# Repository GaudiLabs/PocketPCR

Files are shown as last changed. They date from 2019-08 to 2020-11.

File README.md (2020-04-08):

# PocketPCR
Pocket size USB powered PCR Thermo Cycler.

For more information see project website:
http://gaudi.ch/PocketPCR/

Designed by GaudiLabs:
http://www.gaudi.ch/GaudiLabs/

Support the development of Open Science Hardware:
https://gaudishop.ch/

### License

PocketPCR, all design files and software are licensed under a GNU GENERAL PUBLIC LICENSE
See license file in the repository.

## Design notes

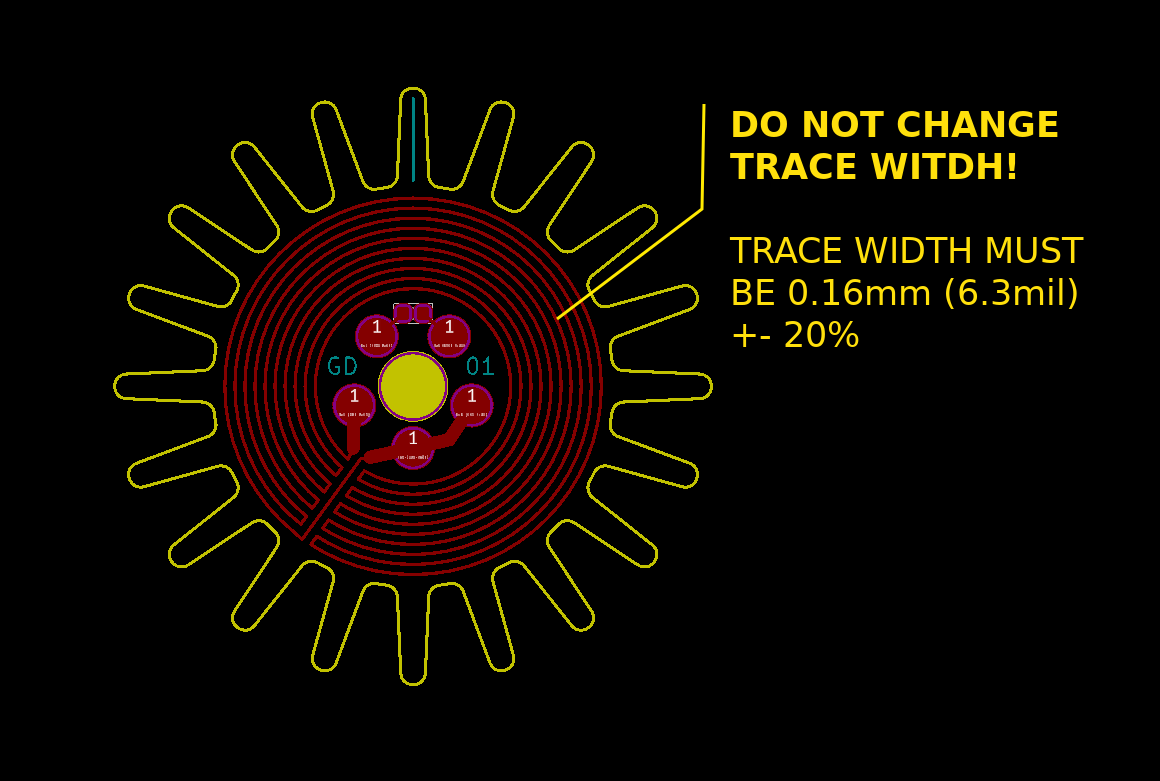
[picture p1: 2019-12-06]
PCB_Layouts/PocketPCR_BottomHeater/Gerber/ProductionFiles/w16496axn77/yg/W16496AXN77_PCR_BottomHeater/W16496AXN77_PCR_BottomHeater/Production_Note.png

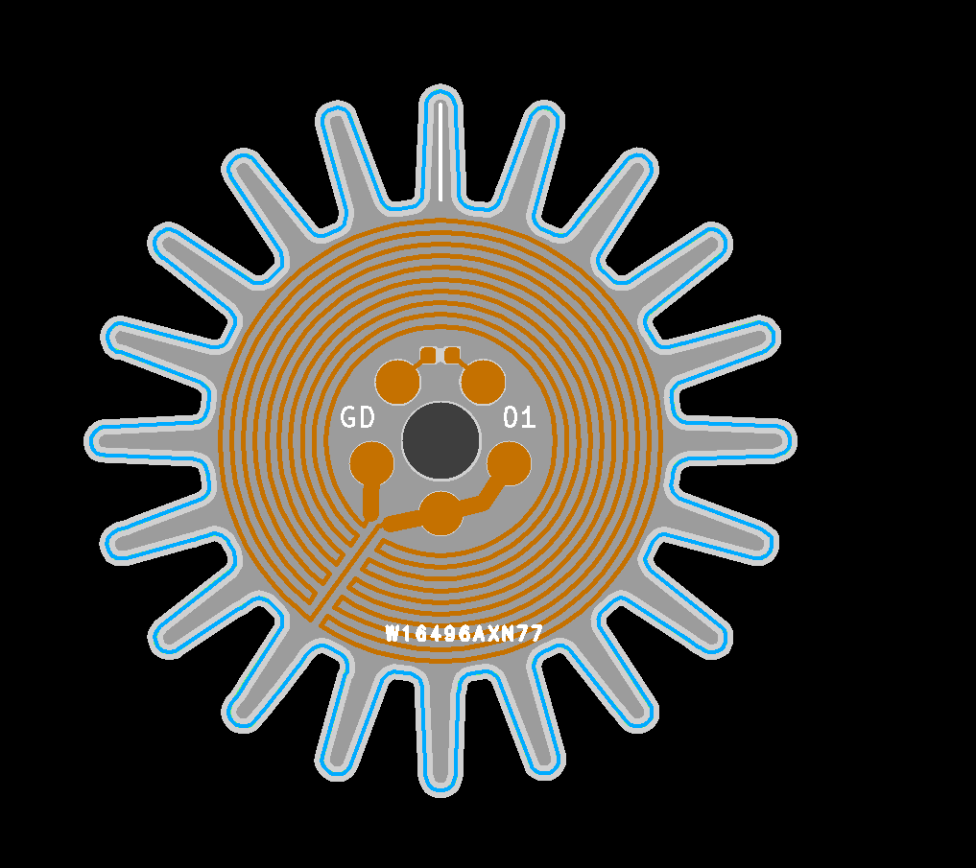
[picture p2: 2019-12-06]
PCB_Layouts/PocketPCR_BottomHeater/BottomHeaterProductionFiles.png

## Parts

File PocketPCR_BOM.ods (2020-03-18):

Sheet: RocketPCR
BOM PocketPCR |  | 19. February 2020
Designator | Quantity | Designation | Package | Order No
U2 | 1 | SAMD21G18B-A changed from SAML21 | TQFP-48_7x7mm_Pitch0.5mm | 556-ATSAMD21G18A-AUT
S1 | 1 | OLED Connector |  | 649-SFV30R-1STE1HLF
Y1 | 1 | Crystal 32.765 | Crystal_SMD_3215-2pin_3.2x1.5mm | 520-ECS-327-12.5-34B 449-LFXTAL009678REEL
LED2,LED1 | 2 | LED | LED-0805
U1 | 1 | TLV1117-33 | SOT-223 | 595-TLV1117LV33DCYR
Q2,Q1,Q3 | 3 | Q_NMOS_GSD | SOT-23 | 863-NTR3C21NZT1G
C3 | 1 | 100uF,6.3V | C_1206_3216Metric | JMK316ABJ107ML-T
C2,C5 | 2 | 10uF, 6.3V | C_1206_3216Metric | JMK107ABJ106MA-T
C1,C4,C12,C14,C16 | 5 | 1uF | C_0805_2012Metric | 810-C2012X7R1C105M-3 603-CC805KKX7R7BB105
C6,C7,C8,C9 | 4 | 100nF | C_0805_2012Metric
C10,C11 | 2 | 22pF | C_0805_2012Metric
C15,C17 | 2 | 2.2uF | C_0805_2012Metric | 603-CC805KKX7R7BB225
R1,R9,R10 | 1 | 4.7k | R_0805_2012Metric
R2,R3 | 2 | 390Ohm | R_0805_2012Metric
R5, R7 | 2 | 390k | R_0805_2012Metric
R4, R6 | 1 | 4.7k 0.1% |  | 279-CPF0805B4K7E1
J3 | 1 | USB_C_Receptacle | USB_C_Receptacle_Amphenol_12401610E4-2A | 523-12401610E4#2A
NTC | 1 | NTC-Thermistoren 0402 10K OHM 0.5% |  | 810-NTCG103JX103DTDS
S1 | 1 | OLED_DISPLAY | OLED_096_1_Flip
J2 | 0 | Conn_02x05_Odd_Even | Pin_Header_Straight_2x05_Pitch1.27mm_SMD
PCB1 | 1 | TopHeater PCB | Alluminium Board, Conductivity 2W, 1.6mm, Black
PCB2 | 1 | PocketPCR PCB | FR4, Black, Thickness 1.6mm
PCB3 | 1 | Lid PCB | FR4, White,Thickness 1.2mm
X1 | 2 | Distanzhülsen, Metall, 6-Kant, M3, 10mm |  | VT DI 10MM
X2 | 2 | Distanzhülsen, Metall, 6-Kant, M3, 20mm |  | VT DI 20MM
SW1 | 1 | Rotary_Encoder_Switch | RotaryEncoder_Alps_EC11E-Switch_Vertical_H20mm | 858-EN11-HSB1AQ15
 | 1 | Encoder Cap | 100Pcs Potentiometer Volume Control/ Switch Knobs Kits 6mm (1/4inch) Shaft
 | 1 | Spring |  | Wire Dia: 0.4mm / Length: 5 mm Or Wire Dia: 0.3mm / Length: 10 mm
 | 1 | Plastic Screw | White Nylon Insulating Countersunk Flat Phillips head Screw M2.5 M3 M4 | M3*6mm
 | 1 | Plastic Screw | 25 BLACK Nylon Plastic M3 M4 M5 and M6 Thumbscrews Knurled + Slotted Thumb Screw | Screw Length: 25mm / M3
 | 2 | Screw | Linsenkopfschraube mit Kreuzschlitz M 3 x 6 DIN 7985 Edelstahl Schwarz 100 Stk.
 | 4 | Screw | Linsenkopfschraube mit Kreuzschlitz M 3 x 16 DIN 7985 Edelstahl Schwarz 100 Stk.
 | 4 | Feets | MAKSEY Rubber Male Hole caps Silicone T type Plug Stopper 6.5mm 7mm 7.5mm 8mm 8.5m Plastic Round Test Tube end caps Gap Masking | Black + 2.7mm
 | 1 | Blower | DIY Reprap 3010 fan 30MM 30x30x10MM 12V 5V 2Pin DC Cooler Small Cooling Fan For 3D Pinter | 5V
J1 | 1 | Conn_01x02_Male | PinHeader_1x02_P2.54mm_Vertical
 | 1 | Beutel ESD | ESD PE-Abschirmbeutel, wiederverschließbar, 76 x 127 mm | ESD BEUTEL-S 127
 | 1 | Heat Block | Aluminium Rund EN AW-6082, gezogen 20 mm | 19.5mm

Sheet: RocketPCR_2
BOM PocketPCR
Designator | Quantity | Designation | Package | Order No | Unit Price | Price
U2 | 1 | SAMD21G18B-A changed from SAML21 | TQFP-48_7x7mm_Pitch0.5mm | 556-ATSAMD21G18A-AUT | 3.16 | 3.16
S1 | 1 | OLED_DISPLAY | OLED_096_1_Flip |  | 3 | 3
 | 1 | TopHeater |  | 19.5mm | 2.5 | 2.5
J3 | 1 | USB_C_Receptacle | USB_C_Receptacle_Amphenol_12401610E4-2A | 523-12401610E4#2A | 1.94 | 1.94
SW1 | 1 | Rotary_Encoder_Switch | RotaryEncoder_Alps_EC11E-Switch_Vertical_H20mm | 858-EN11-HSB1AQ15 | 1.71 | 1.71
S1 | 1 | OLED Connector |  | 649-SFV30R-1STE1HLF | 0.85 | 0.85
PCB2 | 1 | PocketPCR PCB |  |  | 0.825 | 0.825
Q2,Q1,Q3 | 3 | Q_NMOS_GSD | SOT-23 | 863-NTR3C21NZT1G | 0.264 | 0.792
 | 1 | Blower | DIY Reprap 3010 fan 30MM 30x30x10MM 12V 5V 2Pin DC Cooler Small Cooling Fan For 3D Pinter | 5V | 0.65 | 0.65
X2 | 2 | Distanzhülsen, Metall, 6-Kant, M3, 20mm |  | VT DI 20MM | 0.297 | 0.594
U1 | 1 | TLV1117-33 | SOT-223 | 595-TLV1117LV33DCYR | 0.547 | 0.547
PCB1 | 1 | TopHeater PCB |  |  | 0.5 | 0.5
C15,C17 | 2 | 2.2uF | C_0805_2012Metric | 603-CC805KKX7R7BB225 | 0.233 | 0.466
 | 4 | Feets | MAKSEY Rubber Male Hole caps Silicone T type Plug Stopper 6.5mm 7mm 7.5mm 8mm 8.5m Plastic Round Test Tube end caps Gap Masking | Black + 2.7mm | 0.1 | 0.4
Y1 | 1 | Crystal 32.765 | Crystal_SMD_3215-2pin_3.2x1.5mm | 449-LFXTAL009678REEL | 0.398 | 0.398
 | 4 | Screw | Linsenkopfschraube mit Kreuzschlitz M 3 x 16 DIN 7985 Edelstahl Schwarz 100 Stk. |  | 0.09845 | 0.3938
X1 | 2 | Distanzhülsen, Metall, 6-Kant, M3, 10mm |  | VT DI 10MM | 0.143 | 0.286
 | 1 | Spring |  |  | 0.279 | 0.279
C4,C1,C12,C14,C16 | 5 | 1uF | C_0805_2012Metric |  | 0.05 | 0.25
PCB3 | 1 | Lid PCB |  |  | 0.25 | 0.25
 | 1 | Plastic Screw | 25 BLACK Nylon Plastic M3 M4 M5 and M6 Thumbscrews Knurled + Slotted Thumb Screw | Screw Length: 25mm / M3 | 0.2268 | 0.2268
C6,C7,C8,C9 | 4 | 100nF | C_0805_2012Metric |  | 0.05 | 0.2
 | 2 | Screw | Linsenkopfschraube mit Kreuzschlitz M 3 x 6 DIN 7985 Edelstahl Schwarz 100 Stk. |  | 0.09845 | 0.1969
 | 1 | NTC-Thermistoren 0402 10K OHM 0.5% |  | 810-NTCG103JX103DTDS | 0.18 | 0.18
 | 1 | Encoder Cap | 100Pcs Potentiometer Volume Control/ Switch Knobs Kits 6mm (1/4inch) Shaft |  | 0.1654 | 0.1654
R4 | 1 | 4.7k 0.1% |  | 279-CPF0805B4K7E1 | 0.149 | 0.149
C10,C11 | 2 | 22pF | C_0805_2012Metric |  | 0.05 | 0.1
C2 | 1 | 100uF,35V | C_1206_3216Metric |  | 0.1 | 0.1
C3,C5 | 2 | 22uF | C_1206_3216Metric |  | 0.05 | 0.1
 | 1 | Plastic Screw | White Nylon Insulating Countersunk Flat Phillips head Screw M2.5 M3 M4 | M3*6mm | 0.0598 | 0.0598
R2,R3 | 2 | 390Ohm | R_0805_2012Metric |  | 0.01 | 0.02
R9,R10 | 2 | 5k | R_0805_2012Metric |  | 0.01 | 0.02
R1 | 1 | 10k | R_0805_2012Metric |  | 0.01 | 0.01
R5 | 1 | 100k | R_0805_2012Metric |  | 0.01 | 0.01
R7 | 1 | 390k | R_0805_2012Metric |  | 0.01 | 0.01
J1 | 1 | Conn_01x02_Male | PinHeader_1x02_P2.54mm_Vertical |  |  | 0
J2 | 1 | Conn_02x05_Odd_Even | Pin_Header_Straight_2x05_Pitch1.27mm_SMD |  |  | 0
LED2,LED1 | 2 | LED | LED-0805 |  |  | 0
 |  |  |  |  |  | 0
 |  |  |  |  | 18.9739 | 21.3387
 |  |  |  |  |  | 0.576417494973921

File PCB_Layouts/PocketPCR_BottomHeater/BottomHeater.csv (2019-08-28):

Id | Designator | Package | Quantity | Designation | Supplier and ref
1 | D2 | LCC3_SMD | 1 | APD
2 | C1 | C_0805_HandSoldering | 1 | 1uF
3 | C2 | C_0805_HandSoldering | 1 | 0.047uF/200 V(smaller)
4 | C3 | C_0805_HandSoldering | 1 | 0.1uF / 200V
5 | C4 | C_0805_HandSoldering | 1 | 0.22uF
6 | C5 | C_0805_HandSoldering | 1 | 0.1uF
7 | C6 | C_0805_HandSoldering | 1 | 0.5-1pF
8 | R1 | R_0805_HandSoldering | 1 | 4k
9 | R2,R3 | R_0805_HandSoldering | 2 | 1.2M (0)
10 | R4 | R_0805_HandSoldering | 1 | 3.3k
11 | R5 | R_0805_HandSoldering | 1 | 2.2M (1M)
12 | R6 | R_0805_HandSoldering | 1 | 24.9k
13 | R7 | R_0805_HandSoldering | 1 | 20k (higher?)
14 | R8 | R_0805_HandSoldering | 1 | 32.4k
15 | R9,R10 | R_0805_HandSoldering | 2 | 100k
16 | U1 | QFN-12_4x4 | 1 | MAX1932
17 | VREF | PAD_SMD_3mm | 1 | AREF
18 | JP2,JP1 | GS3 | 2 | Jumper_NC_Dual
19 | D1 | SMB_Handsoldering | 1 | 220V
20 | D3 | TOPLED | 1 | LED
21 | L1 | Choke_SMD_7.3x7.3_H3.5 | 1 | 250uH / 0.1A
22 | R11 | R_0805_HandSoldering | 1 | <1G Ohm
23 | SW1 | PUSH_BUTTON_SMD | 1 | BUT
24 | SW2 | DC_JACK_SMD | 1 | DC_JACK
25 | U2 | ARDUINO_MICRO_SMD | 1 | ARDUINO_MICRO
26 | U3 | SOIC-08_N | 1 | OPA656
27 | VBIAS | PAD_SMD_3mm | 1 | VBiasM
28 | GND | PAD_SMD_3mm | 1 | GND
29 | N1,N2 | SOT-23 | 2 | BSS131
30 | R12 | R_0805_HandSoldering | 1 | 10k
31 | TH1 | R_0805_HandSoldering | 1 | Thermistor_NTC 10k
32 | X2 | PAD_SMD_4x2mm | 1 | P+
33 | X3 | PAD_SMD_4x2mm | 1 | P-
34 | G***,G*** | OpenAPD_Photonpack2 | 2 | LOGO
35 | G*** | OpenHardwareLogo | 1 | LOGO
36 | BLOW- | PAD_SMD_3mm | 1 | BLOWER+
37 | BLOW+ | PAD_SMD_3mm | 1 | BLOWER-

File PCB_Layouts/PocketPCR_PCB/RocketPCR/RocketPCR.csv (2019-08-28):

Id | Designator | Package | Quantity | Designation | Supplier and ref
1 | L1 | L_1206_3216Metric | 1 | L
2 | U2 | TQFP-48_7x7mm_Pitch0.5mm | 1 | SAMD21G18B-A changed from SAML21
3 | S1 | OLED_096_1_Flip | 1 | OLED_DISPLAY
4 | Y1 | Crystal_SMD_3215-2pin_3.2x1.5mm | 1 | 32.765
5 | LED2,LED1 | LED-0805 | 2 | LED
6 | U1 | SOT-223 | 1 | TLV1117-33
7 | J3 | USB_C_Receptacle_Amphenol_12401610E4-2A | 1 | USB_C_Receptacle
8 | J2 | Pin_Header_Straight_2x05_Pitch1.27mm_SMD | 1 | Conn_02x05_Odd_Even
9 | SW1 | RotaryEncoder_Alps_EC11E-Switch_Vertical_H20mm | 1 | Rotary_Encoder_Switch
10 | Q2,Q1,Q3 | SOT-23 | 3 | Q_NMOS_GSD
11 | J1 | PinHeader_1x02_P2.54mm_Vertical | 1 | Conn_01x02_Male
12 | C2 | C_1206_3216Metric | 1 | 100uF,35V
13 | C3,C5 | C_1206_3216Metric | 2 | 22uF
14 | C4,C1,C12,C14,C16 | C_0805_2012Metric | 5 | 1uF
15 | C6,C7,C8,C9 | C_0805_2012Metric | 4 | 100nF
16 | R4,R7 | R_0805_2012Metric | 2 | 390k
17 | C10,C11 | C_0805_2012Metric | 2 | 22pF
18 | C15,C17 | C_0805_2012Metric | 2 | 2.2uF
19 | R1 | R_0805_2012Metric | 1 | 10k
20 | R2,R3 | R_0805_2012Metric | 2 | 390
21 | R9,R10 | R_0805_2012Metric | 2 | 5k
22 | X3,X1,X2,X4,X5,X6,X7 | SolderPad1_8mm | 7 | PAD
23 | G*** | GaudiLabs_8 | 1 | LOGO
24 | R5 | R_0805_2012Metric | 1 | 100k
25 | D1 | D_1210_3225Metric | 1 | DIODE
26 | X9,X10,X11 | Fiducial_Cooper | 3 | PAD

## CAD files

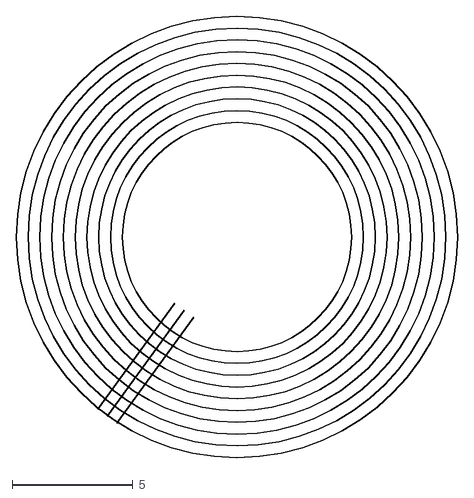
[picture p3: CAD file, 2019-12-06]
PCB_Layouts/PocketPCR_BottomHeater/svg/BottomHeater_traces.dxf
18.3 x 18.3

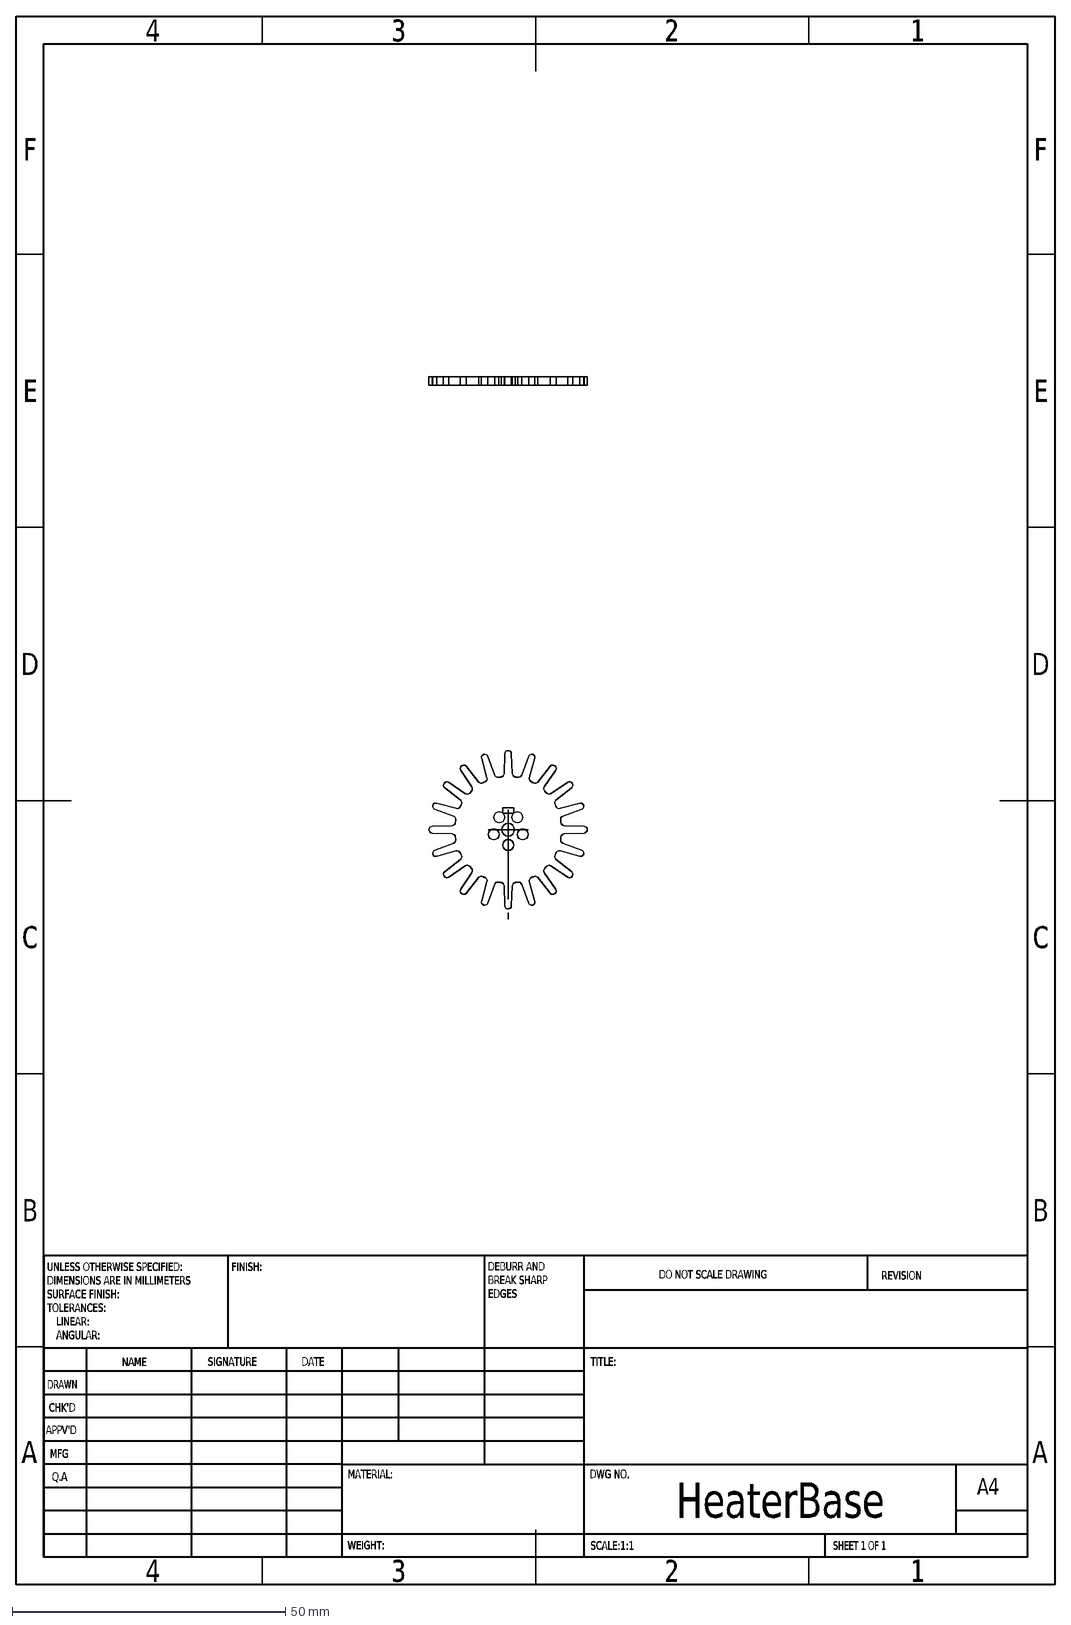
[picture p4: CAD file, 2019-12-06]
PCB_Layouts/PocketPCR_BottomHeater/svg/HeaterBase.DXF
A
B
C
D
E
F
4
3
2
1
DRAWN
CHK'D
APPV'D
MFG
Q.A
UNLESS OTHERWISE SPECIFIED:
DIMENSIONS ARE IN MILLIMETERS
SURFACE FINISH:
TOLERANCES:
LINEAR:
ANGULAR:
FINISH:
DEBURR AND
BREAK SHARP
EDGES
NAME
SIGNATURE
DATE
MATERIAL:
DO NOT SCALE DRAWING
REVISION
TITLE:
DWG NO.
SCALE:1:1
SHEET 1 OF 1
A4
WEIGHT:
HeaterBase

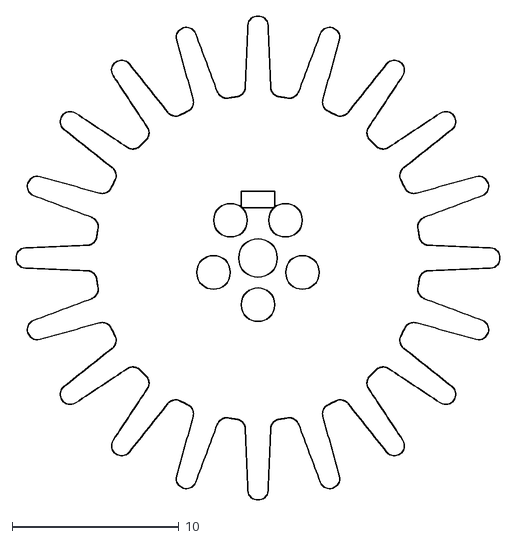
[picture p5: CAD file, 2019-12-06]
PCB_Layouts/PocketPCR_BottomHeater/svg/BottomHeaterOutline.dxf
29.0 x 29.0

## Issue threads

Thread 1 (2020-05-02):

### ISSUE TITLE
Missing dimensions for heat block and PCB thickness

### ISSUE THREAD

**Issue by JamesHagerman** [GaudiLabs/PocketPCR#1]
Hi there,

I would love to build one of these, but I need the dimensions of the aluminum heat block and the thickness of the bottom heater board.

Can you please share that information?

Thanks!

**Comment by abusakib** [comment]
![pcr_3d](https://user-images.githubusercontent.com/21017059/80335928-9aee0f80-8877-11ea-8b1b-020f78d8c2dd.png)
Successfully converted this kicad file to pcb 
contact with me if you want that

**Comment by JamesHagerman** [comment]
@abusakib You don't really need to post a reply to every GitHub issue to get the point across.

Besides, this design requires 3 PCBs, 2 of which require aluminum substrates instead of regular FR4. It's easy enough to load the KiCad files from this repo into PCBWay and place an order... but the Al substrate boards are honestly prohibitively expensive unless you're sourcing them in bulk.

That said, the dimensions I was looking for were committed on March 18 so I'm going to close this issue! Thank you @GaudiLabs for all your work on this!

https://github.com/GaudiLabs/PocketPCR/blob/master/Parts/PocketPCRHeater_V1.PDF

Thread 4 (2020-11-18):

### ISSUE TITLE
Alternating blank lines on LCD Display

### ISSUE THREAD

**Issue by vektorious** [GaudiLabs/PocketPCR#4]
Thanks for this amazing little thing! I already did some runs and I'm more than happy with the results.

However, I have some problems with my OLED display. It appears like every second line is missing/blank. This makes it hard to read the numbers and I often had to go back to zero and count upwards (pictures attached) to set temps and times.

From what I found by searching for this problem online was that it might be a software/driver problem. What do you think?

![IMG_20200422_084346](https://user-images.githubusercontent.com/20026476/80061269-1b87d580-8531-11ea-97b4-8ec5d6a065c1.jpg)
![IMG_20200422_085925](https://user-images.githubusercontent.com/20026476/80061276-204c8980-8531-11ea-9b97-f79e9a48c2a3.jpg)

**Comment by GaudiLabs** [comment]
Hi Alexander

I am sorry for that. I dont think its software. I think it must be a problem with the display connector. Try if you can re-plug the flat cable that goes to the connector on the backside of the board. Or then I will send you a new board. 


Best, 
Urs



On 23 April 2020 07:15:05 CEST, Alexander Kutschera <notifications@github.com> wrote:
>Thanks for this amazing little thing! I already did some runs and I'm
>more than happy with the results.
>
>However, I have some problems with my OLED display. It appears like
>every second line is missing/blank. This makes it hard to read the
>numbers and I often had to go back to zero and count upwards (pictures
>attached) to set temps and times.
>
>From what I found by searching for this problem online was that it
>might be a software/driver problem. What do you think?
>
>![IMG_20200422_084346](https://user-images.githubusercontent.com/20026476/80061269-1b87d580-8531-11ea-97b4-8ec5d6a065c1.jpg)
>![IMG_20200422_085925](https://user-images.githubusercontent.com/20026476/80061276-204c8980-8531-11ea-9b97-f79e9a48c2a3.jpg)
>
>
>-- 
>You are receiving this because you are subscribed to this thread.
>Reply to this email directly or view it on GitHub:
>https://github.com/GaudiLabs/PocketPCR/issues/4

-- 
Sent from my Android device with K-9 Mail. Please excuse my brevity.

**Comment by vektorious** [comment]
Hey Urs,

I tried un- and re-plugging the display and did not see any improvement. But, I saw that some connector pins are soldered together (accidentally?). That's probably the cause of the problem. I have to find some desoldering wick and try to fix it. What do you think?

Thanks for the help!

Alex

![IMG_20200425_065008](https://user-images.githubusercontent.com/20026476/80274106-524c2000-86d8-11ea-99b3-150cd36e682d.jpg)

**Comment by GaudiLabs** [comment]
Sure, resoldering the connector pins will probably fix it. Try also to retouch the other ones as there might be a pin not properly soldered. And dont worry if anything goes wrong, a new board is ready to be shipped to you here.

Urs

On 25 April 2020 09:44:02 CEST, Alexander Kutschera <notifications@github.com> wrote:
>Hey Urs,
>
>I tried un- and re-plugging the display and did not see any
>improvement. But, I saw that some connector pins are soldered together
>(accidentally?). That's probably the cause of the problem. I have to
>find some desoldering wick and try to fix it. What do you think?
>
>Thanks for the help!
>
>Alex
>
>![IMG_20200425_065008](https://user-images.githubusercontent.com/20026476/80274106-524c2000-86d8-11ea-99b3-150cd36e682d.jpg)
>
>
>-- 
>You are receiving this because you commented.
>Reply to this email directly or view it on GitHub:
>https://github.com/GaudiLabs/PocketPCR/issues/4#issuecomment-619337060

-- 
Sent from my Android device with K-9 Mail. Please excuse my brevity.

**Comment by vektorious** [comment]
Hey Urs,

I tried hard but so far, I could not resolder the pins. I afraid I have to make use of your offer...
Should I send you my contact details via mail?

Thanks in advance!

Alex

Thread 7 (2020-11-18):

### ISSUE TITLE
uploading/modifying code

### ISSUE THREAD

**Issue by aaron4444** [GaudiLabs/PocketPCR#7]
Hi. just received mine and i was hoping to make a small modification. Could i ask for maybe a quick few lines on how to upload the modified code with arduino?

**Comment by aaron4444** [comment]
sorry, i also see that the current code version is 1.2.2020, can i ask for the most recent version? thank you again for your time.

**Comment by GaudiLabs** [comment]
Hi

Nice, what modification do you plan to do? The PocketPCR is compatibe with the Adafruit Feather M0. So you can see here how to install the board in the Arduino IDE:

https://learn.adafruit.com/adafruit-feather-m0-basic-proto/

Good Luck,
Urs

On 17 November 2020 02:57:46 CET, aaron4444 <notifications@github.com> wrote:
>Hi. just received mine and i was hoping to make a small modification.
>Could i ask for maybe a quick few lines on how to upload the modified
>code with arduino? 
>
>-- 
>You are receiving this because you are subscribed to this thread.
>Reply to this email directly or view it on GitHub:
>https://github.com/GaudiLabs/PocketPCR/issues/7

-- 
Sent from my Android device with K-9 Mail. Please excuse my brevity.

**Comment by aaron4444** [comment]
hi. thank you for your response. 

-  i wanted to be able to give it a recipe that has more steps than typical PCR. so i want to give it steps like 50, 49.5, 49, 48.5 etc. down to room temp. I figure i add a menu item to read a recipe? usually its a start point and an endpoint with a ramp typically between 1 and 0.2 degrees per step. 
 
- I would like to setup serial communication with the computer, to take commands like: heat to this temp.

the next ones are kinda outside of pcr a little. i do dna crytal growth, so i have a camera that i want to do in situ microscopy with. I can see em growing so i was planning to try to trigger from the pocketpcr when it reaches the right temperature to take a picture, or a series of pictures.

**Comment by aaron4444** [comment]
Sorry if this isn't the place to debug. Can't seem to get the ssd1306 library to work. Can you share the version of that library you are using? 


**PocketPCR_V2_quite_dev_i:76:74: error: call of overloaded 'Adafruit_SSD1306(int, int, int, int, int)' is ambiguous**
   76 | Adafruit_SSD1306 display( OLED_MOSI,OLED_CLK,OLED_DC, OLED_RESET, OLED_CS);
      |                                                                          ^
In file included from C:\Users\Aaron-Crucial-2016\Downloads\PocketPCR-master (1)\PocketPCR-master\code\PocketPCR_V2_quite_dev_i\PocketPCR_V2_quite_dev_i.ino:13:
C:\Users\Aaron-Crucial-2016\Documents\Arduino\libraries\Adafruit_SSD1306/Adafruit_SSD1306.h:138:3: note: candidate: 'Adafruit_SSD1306::Adafruit_SSD1306(int8_t, int8_t, int8_t, int8_t, int8_t)'
  138 |   Adafruit_SSD1306(int8_t mosi_pin, int8_t sclk_pin, int8_t dc_pin,
      |   ^~~~~~~~~~~~~~~~
C:\Users\Aaron-Crucial-2016\Documents\Arduino\libraries\Adafruit_SSD1306/Adafruit_SSD1306.h:129:3: note: candidate: 'Adafruit_SSD1306::Adafruit_SSD1306(uint8_t, uint8_t, TwoWire*, int8_t, uint32_t, uint32_t)'
  129 |   Adafruit_SSD1306(uint8_t w, uint8_t h, TwoWire *twi = &Wire,
      |   ^~~~~~~~~~~~~~~~
Multiple libraries were found for "Adafruit_ZeroDMA.h"
 Used: C:\Users\Aaron-Crucial-2016\AppData\Local\Arduino15\packages\adafruit\hardware\samd\1.6.4\libraries\Adafruit_ZeroDMA
 Not used: C:\Users\Aaron-Crucial-2016\Documents\Arduino\libraries\Adafruit_Zero_DMA_Library
exit status 1
call of overloaded 'Adafruit_SSD1306(int, int, int, int, int)' is ambiguous

**Comment by GaudiLabs** [comment]
Had used an older version of the Adafruit Display Library. Fixed that, just this line that changed:
Adafruit_SSD1306 display(SCREEN_WIDTH, SCREEN_HEIGHT, OLED_MOSI, OLED_CLK, OLED_DC, OLED_RESET, OLED_CS);

Now the current Adafruit_SSD1306 Library should be good to go:
https://github.com/adafruit/Adafruit_SSD1306

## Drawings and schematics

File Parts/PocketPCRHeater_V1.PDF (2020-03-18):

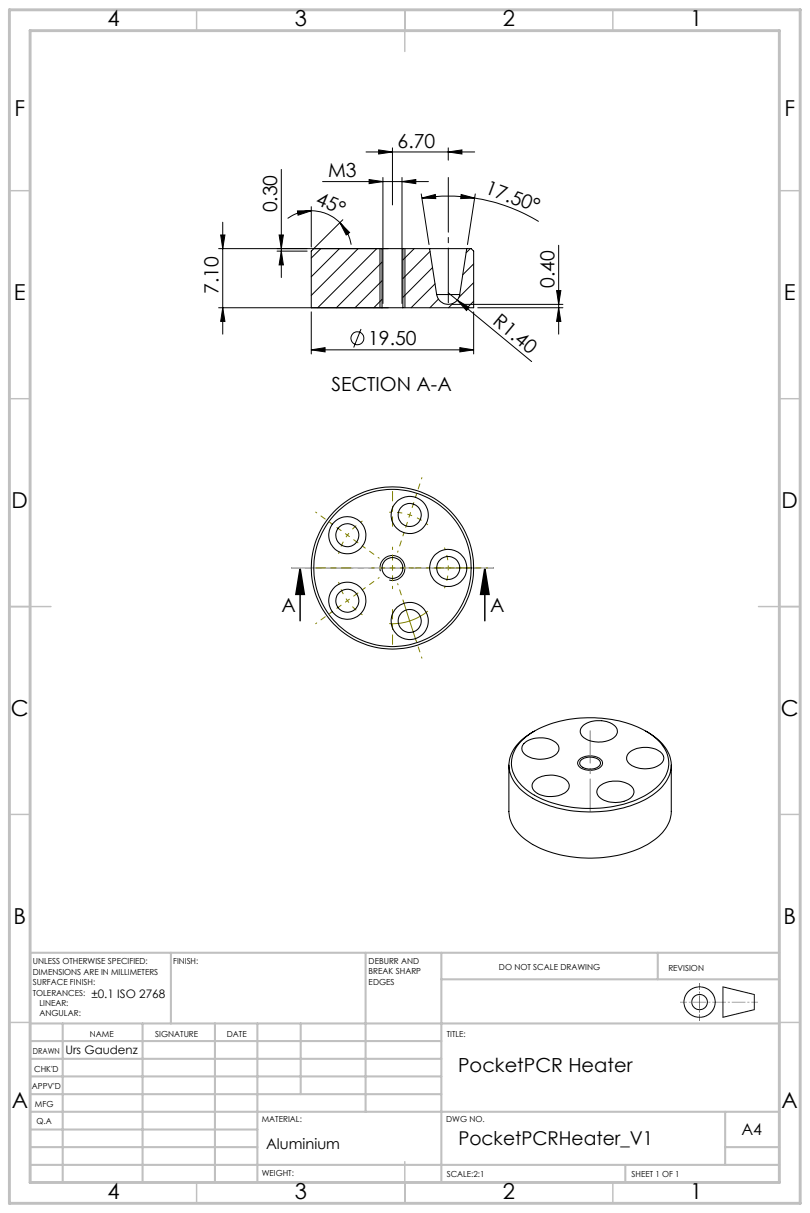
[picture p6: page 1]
SECTION A-A; ±0.1 ISO 2768; FINISH:; DEBURR AND; BREAK SHARP; DO NOT SCALE DRAWING; REVISION; SCALE:2:1; SHEET 1 OF 1

UNLESS OTHERWISE SPECIFIED:
DIMENSIONS ARE IN MILLIMETERS
SURFACE FINISH:
TOLERANCES:
LINEAR:
ANGULAR:

NAME | SIGNATURE | DATE | | | | TITLE: PocketPCR Heater

DRAWN | Urs Gaudenz

CHK'D
APPV'D
MFG
Q.A | | | | MATERIAL: Aluminium | DWG NO. PocketPCRHeater_V1 | A4

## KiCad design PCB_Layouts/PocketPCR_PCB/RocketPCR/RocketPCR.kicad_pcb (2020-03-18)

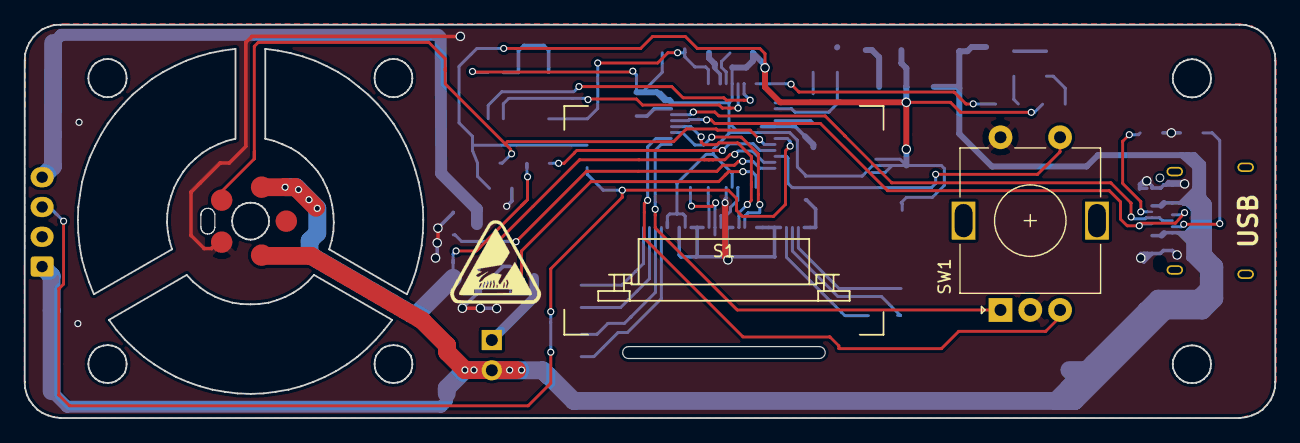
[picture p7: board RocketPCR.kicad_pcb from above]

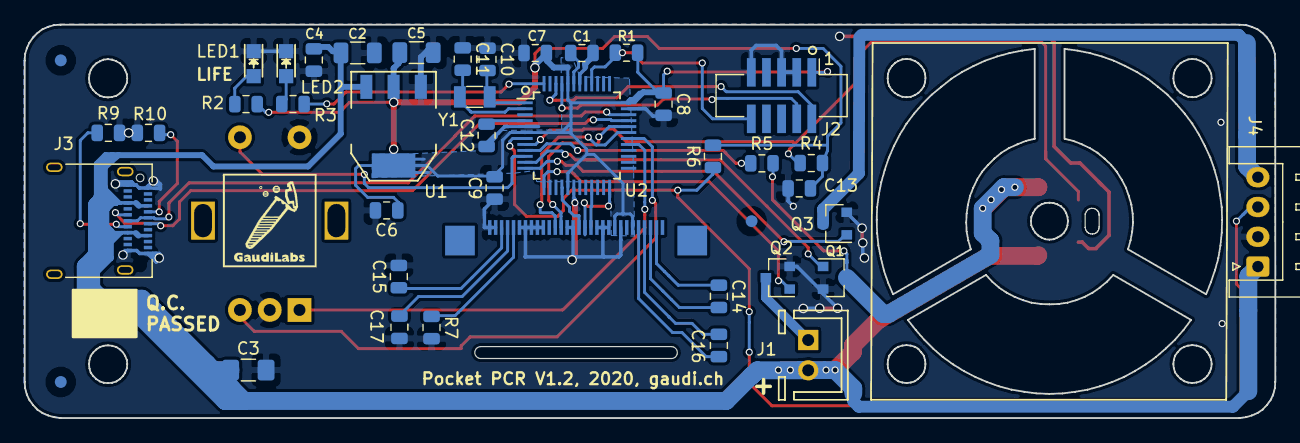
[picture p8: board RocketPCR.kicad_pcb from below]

Board: 2 copper layers, 105.0 x 33.0 mm, 48 parts (41 on the bottom side), 41 nets.

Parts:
C1, C4, C12, C14, C16: 1uF; C_0805_2012Metric
C2: 100uF,35V; C_1206_3216Metric
C3: 22uF; C_1206_3216Metric_Pad1.42x1.75mm_HandSolder
C5: 22uF; C_1206_3216Metric
C6, C7, C8, C9, C13: 100nF; C_0805_2012Metric
C10, C11: 22pF; C_0805_2012Metric
C15, C17: 2.2uF; C_0805_2012Metric
J1: Conn_01x02_Male; PinHeader_JST_1x02_P2.54mm_Vertical
J2: Conn_02x05_Odd_Even; Pin_Header_Straight_2x05_Pitch1.27mm_SMD
J3: USB_C_Receptacle; USB_C_Receptacle_Amphenol_12401610E4-2A
J4: Conn_01x04_Female; JST_XH_S04B-XH-A_1x04_P2.50mm_Horizontal
LED1, LED2: LED; LED-0805
Q1, Q2, Q3: Q_NMOS_GSD; SOT-23
R1: 10k; R_0805_2012Metric
R2, R3: 390; R_0805_2012Metric
R4, R6: 4.7k; R_0805_2012Metric
R5, R7: 390k; R_0805_2012Metric
R9, R10: 5k; R_0805_2012Metric
S1: OLED_DISPLAY; OLED_096_1_Flip
SW1: Rotary_Encoder_Switch; RotaryEncoder_Alps_EC11E-Switch_Vertical_H20mm
U1: TLV1117-33; SOT-223
U2: SAMD21G18B-A changed from SAML21; TQFP-48_7x7mm_Pitch0.5mm
X2, X3, X4, X6, X7: PAD; SolderPad1_8mm
X9, X10, X11: PAD; Fiducial_1mm_Dia_2.54mm_Outer_CopperBottom
Y1: 32.765; Crystal_SMD_3215-2pin_3.2x1.5mm

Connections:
+3V3: C5.1, C6.1, C7.1, C8.1, C9.2, C13.2, J2.1, R1.2, R2.1, R4.2, R6.2, S1.6, S1.9, U1.2, U2.6, U2.17, U2.36, U2.44
AREF: C12.2, U2.4
BLOCK: Q1.1, U2.11
D+: J3.A6, J3.B6, U2.34
D-: J3.A7, J3.B7, U2.33
DISP_CS: S1.13, U2.21
DISP_DC: S1.15, U2.16
DISP_RES: S1.14, U2.24
DISP_SCL: S1.18, U2.32
DISP_SDA: S1.19, U2.31
ENC1: SW1.A, U2.29
ENC2: SW1.B, U2.30
FAN: Q2.1, U2.13
GND: C1.2, C2.2, C3.2, C4.1, C5.2, C6.2, C7.2, C8.2, C9.1, C10.1, C11.1, C12.1, C13.1, C15.2, C17.2, J2.3, J2.5, J2.9, J3.A1, J3.A12, J3.B1, J3.B12, J4.2, LED1.1, LED2.1, Q1.2, Q2.2, Q3.2, R7.2, R9.2, R10.2, S1.8, S1.10, S1.11, S1.12, S1.16, S1.17, S1.21, S1.22, S1.23, S1.24, S1.25, S1.29, S1.30, SW1.C, SW1.S2, U1.1, U2.5, U2.18, U2.35, U2.42, X6.1
LID: Q3.1, U2.12
unnamed: C1.1, U2.43
unnamed: C10.2, U2.1, Y1.1
unnamed: C11.2, U2.2, Y1.2
unnamed: C14.1, S1.2
unnamed: C14.2, S1.3
unnamed: C15.1, S1.28
unnamed: C16.1, S1.4
unnamed: C16.2, S1.5
unnamed: C17.1, S1.27
unnamed: J1.1, Q2.3
unnamed: J3.A5, R10.1
unnamed: J3.B5, R9.1
unnamed: J4.4, Q3.3
unnamed: LED1.2, R2.2
unnamed: LED2.2, R3.2
unnamed: R5.1, U2.9
unnamed: R7.1, S1.26
RESET: J2.10, R1.1, U2.40
RX_LED: R3.1, U2.48
SW1: SW1.S1, U2.10
SWCLK: J2.4, U2.45
SWDIO: J2.2, U2.46
TEMP_BLOCK: R4.1, U2.8, X3.1
TEMP_LID: J4.3, R6.1, U2.7
VSENS: Q1.3, R5.2, X2.1
V_USB: C2.1, C3.1, C4.2, J1.2, J3.A4, J3.A9, J3.B4, J3.B9, J4.1, U1.3, X4.1

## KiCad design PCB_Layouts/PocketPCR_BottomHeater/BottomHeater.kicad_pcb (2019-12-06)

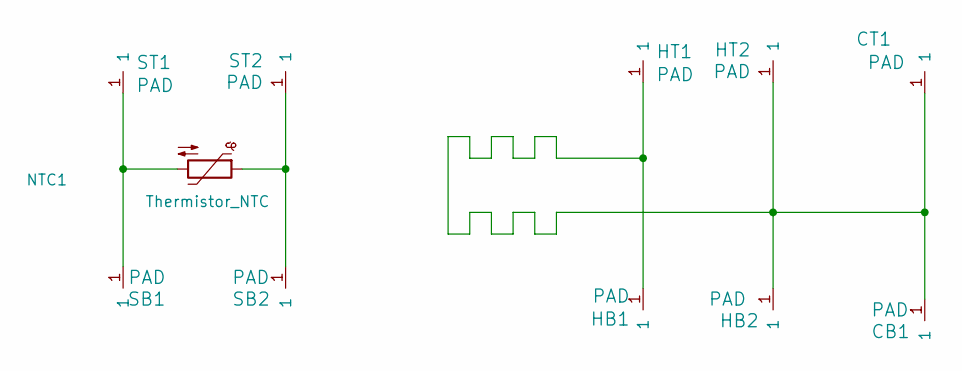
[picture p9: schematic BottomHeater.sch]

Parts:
CB1: PAD; SolderPad1_8mm
CT1: PAD; SolderPad1_8mm
HB1, HB2: PAD; SolderPad1_8mm
HT1, HT2: PAD; SolderPad1_8mm
NTC1: Thermistor_NTC; C_0402_1005Metric
SB1, SB2: PAD; SolderPad1_8mm
ST1, ST2: PAD; SolderPad1_8mm

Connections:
unnamed: CB1.1, CT1.1, HB1.1, HB2.1, HT1.1, HT2.1
unnamed: NTC1.1, SB2.1, ST2.1
unnamed: NTC1.2, SB1.1, ST1.1

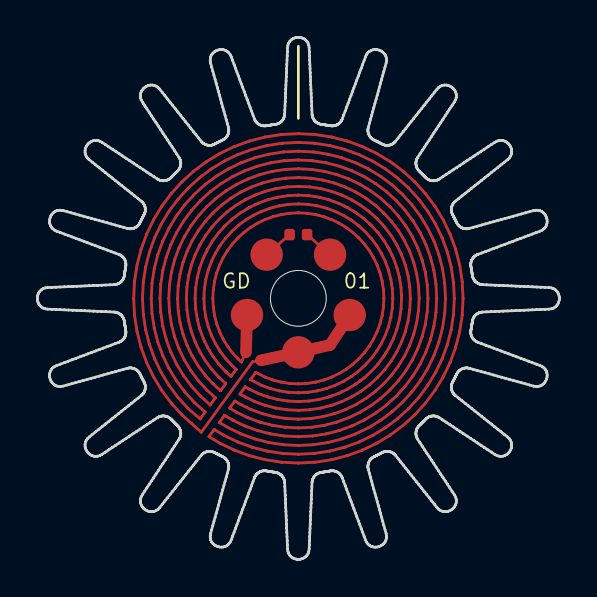
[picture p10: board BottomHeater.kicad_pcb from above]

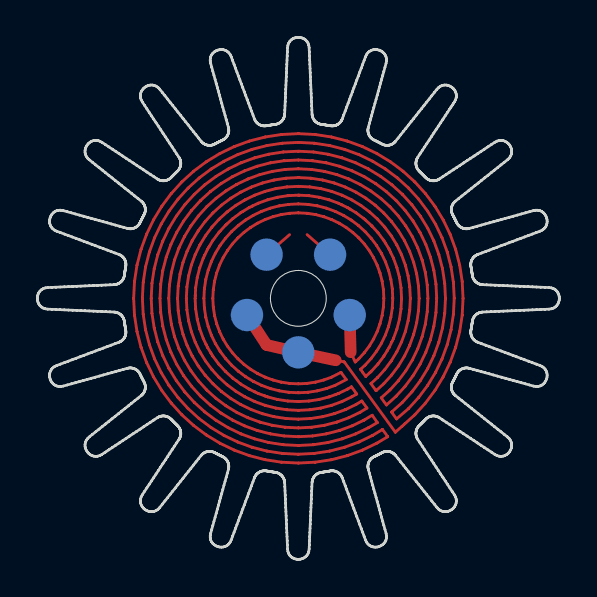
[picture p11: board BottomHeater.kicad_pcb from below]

Board: 2 copper layers, 29.0 x 29.0 mm, 11 parts (5 on the bottom side), 3 nets.

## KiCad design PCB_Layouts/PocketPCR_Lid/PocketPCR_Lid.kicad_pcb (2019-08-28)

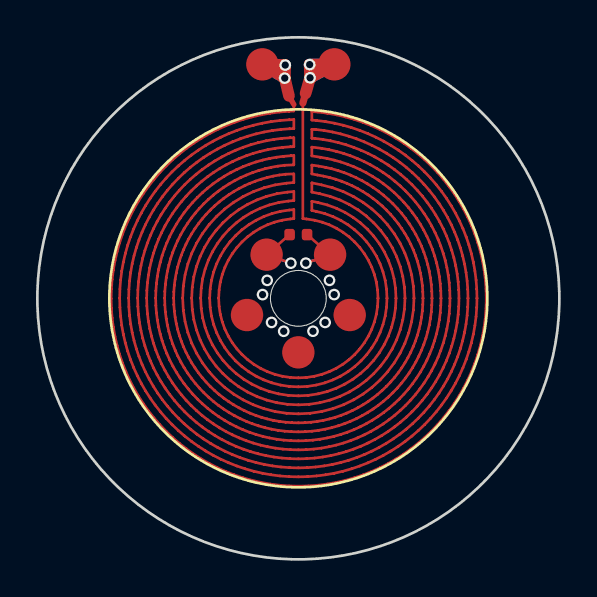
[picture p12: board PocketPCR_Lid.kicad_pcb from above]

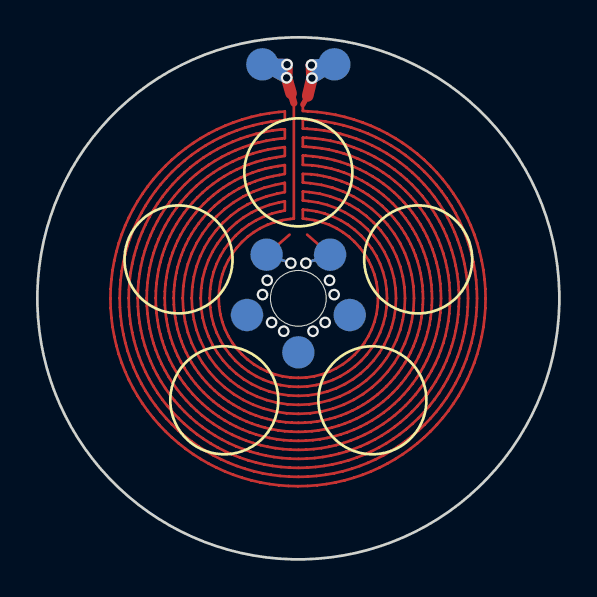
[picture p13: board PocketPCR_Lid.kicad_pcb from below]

Board: 2 copper layers, 29.0 x 29.0 mm, 15 parts (7 on the bottom side), 4 nets.

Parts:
CB1: PAD; SolderPad1_8mm
CT1: PAD; SolderPad1_8mm
HB1, HB2: PAD; SolderPad1_8mm
HT1, HT2: PAD; SolderPad1_8mm
NTC1: Thermistor_NTC; C_0402_1005Metric
SB1, SB2, SB2#2, SB2#3, SB2#4, SB2#5: PAD; SolderPad1_8mm
ST1, ST2: PAD; SolderPad1_8mm

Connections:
unnamed: CB1.1, CT1.1
unnamed: HB1.1, HB2.1, HT1.1, HT2.1
unnamed: NTC1.1, SB2#5.1, ST2.1
unnamed: NTC1.2, SB1.1, ST1.1

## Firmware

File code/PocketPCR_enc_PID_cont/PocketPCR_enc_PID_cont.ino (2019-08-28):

/*
  Analog input, analog output, serial output

  Reads an analog input pin, maps the result to a range from 0 to 255 and uses
  the result to set the pulse width modulation (PWM) of an output pin.
  Also prints the results to the Serial Monitor.

  The circuit:
  - potentiometer connected to analog pin 0.
    Center pin of the potentiometer goes to the analog pin.
    side pins of the potentiometer go to +5V and ground
  - LED connected from digital pin 9 to ground

  created 29 Dec. 2008
  modified 9 Apr 2012
  by Tom Igoe

  This example code is in the public domain.

  http://www.arduino.cc/en/Tutorial/AnalogInOutSerial
*/

#include <math.h> 
#include "Adafruit_GFX.h"
#include <Adafruit_SSD1306.h>
#include "Rotary.h"

#include <Fonts/FreeSans9pt7b.h>

// These constants won't change. They're used to give names to the pins used:
const int analogInPin = A2;  // Analog input pin that the potentiometer is attached to
const int fanPin = 4; // Analog output pin that the LED is attached to
const int heaterPin = 8; // Analog output pin that the LED is attached to
const int lidPin = 9; // Analog output pin that the LED is attached to
const int butPin = A4; // Analog output pin that the LED is attached to

const int NTC_B = 3435;
const float NTC_TN = 298.15;
const int NTC_RN = 10000;
const float NTC_R0 = 4.7;

const float temperature_tollerance=0.5;
// Rotary encoder is wired with the common to ground and the two
// outputs to pins 2 and 3.
#define ENCODER_1 6
#define ENCODER_2 7
Rotary rotary = Rotary(ENCODER_1, ENCODER_2);

// If using software SPI (the default case):
#define OLED_MOSI   20
#define OLED_CLK   21
#define OLED_DC    0 //11
#define OLED_CS    22 //12
#define OLED_RESET 5

#define CASE_Main 1
#define CASE_Settings 2
#define CASE_EditSettings 3
#define CASE_Run 4

#define PCR_set 1
#define PCR_transition 2
#define PCR_time 3
#define PCR_end 4



#define PIDp 0.6
#define PIDi 1
#define PIDd 0.2

#define SETTING_Size 5
String SETTING_String[SETTING_Size] = { "Init", "Denature", "Annealing" , "Extension", "Final" };
int SETTING_Value[SETTING_Size*2];
int SETTING_cycles = 20;

Adafruit_SSD1306 display( OLED_MOSI,OLED_CLK,OLED_DC, OLED_RESET, OLED_CS);

int sensorValue = 0;        // value read from the pot
int outputValue = 0;        // value output to the PWM (analog out)
float temperature =0;
float temperature_mean =0;

float sensorResistance =0;
float sensorVoltage =0;

boolean editMode = false;
boolean minuteMode = false;

int counter = 0;        // value read from the pot

int x=0;
int caseUX = 1; 
int casePCR = 1;
int MenuItem = 1;
int PCRstate = 0;
int PCRcycle = 1;

int PCRpwm = 0;

float TEMPset;
float TEMPdif;
float TEMPcontrol;
float TEMPdif_a[10];
float TEMPd;
long TEMPclick=0;
long TIMEclick=0;
int TIMEcontrol=0;

int heatPower = 191;
int fanPower=0;
void setup() {

  pinMode(ENCODER_1, INPUT_PULLUP);
  pinMode(ENCODER_2, INPUT_PULLUP);
  pinMode(butPin, INPUT_PULLUP);

  pinMode(fanPin, OUTPUT);
  pinMode(heaterPin, OUTPUT);
  pinMode(lidPin, OUTPUT);

  attachInterrupt(ENCODER_1, rotate, CHANGE);
  attachInterrupt(ENCODER_2, rotate, CHANGE);

  // initialize serial communications at 9600 bps:
  Serial.begin(115200);

SETTING_Value[0] = 99;      
SETTING_Value[1] = 60;   

SETTING_Value[2] = 95;      
SETTING_Value[3] = 120;  

SETTING_Value[4] = 55;      
SETTING_Value[5] = 80;  

SETTING_Value[6] = 72;      
SETTING_Value[7] = 40;  

SETTING_Value[8] = 25;      
SETTING_Value[9] = 00;  


    display.begin(SSD1306_SWITCHCAPVCC);

      // Show image buffer on the display hardware.
  // Since the buffer is intialized with an Adafruit splashscreen
  // internally, this will display the splashscreen.

  display.clearDisplay();  
    
 display.setTextSize(1);
 display.setCursor(1,55);
  display.setTextColor(WHITE);
  display.println("V3.2");
      display.dim(false);
  display.display();
   // display.setFont(&FreeMono9pt7b);

   analogReadResolution(12);


    
}

void loop() {
  // read the analog in value:
 // analogReference(AR_EXTERNAL);

analogWrite(fanPin,0);
analogWrite(heaterPin,0);
    delay(20);
sensorValue = analogRead(analogInPin);
  // map it to the range of the analog out:
sensorVoltage=3.3*sensorValue/4096;
sensorResistance=((sensorVoltage*NTC_R0)/(3.3-sensorVoltage));
temperature=  1/(log(sensorResistance*1000/NTC_RN)/NTC_B+1/NTC_TN)-273.15 ;
temperature_mean= (temperature_mean*3+temperature)/4;

  // print the results to the Serial Monitor:
  //Serial.print("sensor = ");
  //  Serial.print(sensorValue);
 // Serial.print("\t output = ");
 // Serial.println(temperature);


      
  // wait 2 milliseconds before the next loop for the analog-to-digital
  // converter to settle after the last reading:
 


if (temperature>105) {
  heatPower=0;
  fanPower=63;
  };
  

     // digitalWrite(heaterPin, HIGH);   // turn the LED on (HIGH is the voltage level)

    //  analogWrite(heaterPin, heatPower);   // turn the LED on (HIGH is the voltage level)
    //  analogWrite(fanPin, fanPower);   // turn the LED on (HIGH is the voltage level)





switch (caseUX) {

case CASE_Main:

  
   if (counter>1) counter=0;
   if (counter<0) counter=1;
   MenuItem = counter;
   draw_main_display();
   
   if (!digitalRead(butPin)) {while (!digitalRead(butPin));
   
   if (MenuItem==0) {caseUX=CASE_Run; PCRstate=0; counter=0;}
   if (MenuItem==1) {caseUX=CASE_Settings; counter=0;}

   }
   
    break;
    
case CASE_Settings:

    if (counter>11) counter=0;
    if (counter<0) counter=11;
    MenuItem = counter;
    if ((MenuItem%2==1)&&(SETTING_Value[MenuItem]>90)) minuteMode=true; else minuteMode=false;
    if (!digitalRead(butPin)) 
    {while (!digitalRead(butPin)); caseUX=CASE_EditSettings; 
    if (minuteMode) counter=SETTING_Value[MenuItem]/60; else counter=SETTING_Value[MenuItem];}
    draw_setup_display();
    
    break;

case CASE_EditSettings:

    
    if (MenuItem%2==0)
     {if (counter<25) counter=25;
      if (counter>99) {counter=99;}

     } // Temp Menu
     
     else
      {if (minuteMode)
       {if (counter<2) {minuteMode=false; counter=90;}
       }  //Minut Mode
       else
       {
       if (counter>90) {minuteMode=true; counter=2;}
       if (counter<0) {counter=0;}
       } //not Minut Mode
      } // Time Menu
    
    if (MenuItem==10) caseUX=CASE_Main;
    if (MenuItem<10) {if (minuteMode) SETTING_Value[MenuItem]=counter*60; else SETTING_Value[MenuItem]=counter;}
    if (!digitalRead(butPin)) {while (!digitalRead(butPin)); caseUX=CASE_Settings;counter=MenuItem;}
    draw_setup_display();
    
    break;

case CASE_Run:

  TEMPdif=TEMPset-temperature_mean;

  if (millis()-TEMPclick>200) {
  TEMPclick=millis();
  TEMPd=TEMPdif_a[4]-TEMPdif;
  TEMPdif_a[4]=TEMPdif_a[3];
  TEMPdif_a[3]=TEMPdif_a[2];
  TEMPdif_a[2]=TEMPdif_a[1];
  TEMPdif_a[1]=TEMPdif_a[0];
  TEMPdif_a[0]=TEMPdif;
    Serial.println (TEMPd);
  }
  
    switch (casePCR) {

    case PCR_set:
    TEMPset=SETTING_Value[PCRstate*2];
    TIMEcontrol=SETTING_Value[1+PCRstate*2];
    casePCR=PCR_transition;
    break;

#define PCR_set 1
#define PCR_transition 2
#define PCR_time 3
#define PCR_end 4

    case PCR_transition:
    
    runPID();
    draw_run_display();
    
    if (abs(TEMPset-temperature_mean)<temperature_tollerance) {TIMEclick=millis(); casePCR=PCR_time;}
    
    break;

    case PCR_time:

    runPID();
    TIMEcontrol=SETTING_Value[1+PCRstate*2]-(millis()-TIMEclick)/1000;
    draw_run_display();

    if (TIMEcontrol<=0) {
    if (PCRstate==3)
    {PCRstate=1;
    PCRcycle++;
    } else
    {PCRstate++;casePCR=PCR_set;};
    casePCR=PCR_set;
    }
    break;
    
    default:
    // Statement(s)
    break;
    }//PCR switch

    break;

default:
    // Statement(s)
    break;
    
} //switch
}




void draw_value_box(int x, int y, int val, bool highlight,bool edit)
{

  display.drawRect(x-3,y+2-val/2,17,val/2-1,1);
  
if (highlight&&!edit){
  display.fillRect(x-3,y+2-val/2,17,11,1);
  display.setTextColor(0);
}
if (highlight&&edit)  display.drawRect(x-2,y+2-val/2,15,11,1);

 display.setCursor(x,y-val/2+4);
 display.println(val);
 display.setTextColor(1);
};

void draw_value(int x, int y, int val, bool highlight,bool edit)
{
if (highlight&&!edit){
  display.fillRect(x-3,y-1,17,12,1);
  display.setTextColor(0);
    display.setCursor(x,y-1);

  } else   display.setCursor(x,y);

 //display.drawRect(x-3,y,2,7,1);
 //display.drawRect(x+12,y,2,7,1);
if (highlight&&edit){
 display.drawLine(x-3,y,x-3,y+6,1);
 display.drawLine(x+13,y,x+13,y+6,1);
}

 // display.drawRect(x-3,y-2,17,11,1);
  
  if (val>90) 
   { display.print(val/60); 
   display.println("m");} else
   {
    display.println(val); 
   }
   display.setTextColor(1);
}

void draw_setup_display()

{
  
display.clearDisplay(); 

 if (MenuItem<10) {
  
display.setCursor(5,0);
//display.print("Set ");
display.print(SETTING_String[MenuItem/2]);
if (MenuItem%2==0) {display.print(" Temp. [");display.print("\xA7");display.print("C]");} else {display.print(" Time "); if (minuteMode) display.print("[min]"); else display.print("[s]");  }

 } else 

 {
 if (MenuItem==11)   // Set or Cancel
 {

 display.setCursor(34,0);
 display.println("Set");
 display.fillRect(70,0,42,9,1);
 display.setTextColor(0);
 display.setCursor(75,1);
 display.println("Cancel");
 display.setTextColor(1);
 } else

 {
  display.fillRect(30,0,25,9,1);
 display.setTextColor(0);
 display.setCursor(34,1);
 display.println("Set");
 display.setTextColor(1);
 display.setCursor(75,0);
 display.println("Cancel");
 
  }
}


draw_value_box (21,55,SETTING_Value[0],MenuItem==0,caseUX==CASE_EditSettings);
draw_value_box (43,55,SETTING_Value[2],MenuItem==2,caseUX==CASE_EditSettings);
draw_value_box (63,55,SETTING_Value[4],MenuItem==4,caseUX==CASE_EditSettings);
draw_value_box (83,55,SETTING_Value[6],MenuItem==6,caseUX==CASE_EditSettings);
draw_value_box (105,55,SETTING_Value[8],MenuItem==8,caseUX==CASE_EditSettings);

draw_value (21,57,SETTING_Value[1],MenuItem==1,caseUX==CASE_EditSettings);
draw_value (43,57,SETTING_Value[3],MenuItem==3,caseUX==CASE_EditSettings);
draw_value (63,57,SETTING_Value[5],MenuItem==5,caseUX==CASE_EditSettings);
draw_value (83,57,SETTING_Value[7],MenuItem==7,caseUX==CASE_EditSettings);
draw_value (105,57,SETTING_Value[9],MenuItem==9,caseUX==CASE_EditSettings);

   

  display.display();
  
 // Serial.println (encoder0Pos, DEC);

    // Serial.println(Enc_counter,DEC);
   // Serial.print(millis());
   //    Serial.print(" :");
  //   Serial.println(temperature,DEC);
  
  
  }

void draw_main_display()
{
display.clearDisplay(); 

   display.setFont(&FreeSans9pt7b);


   if (MenuItem==0)   // Set or Cancel
 {

  display.fillRect(21,10,86,25,1);
 display.setTextColor(0);
 display.setCursor(26,28);
 display.println("Run PCR");

 //display.fillRect(21,38,86,25,1);
 display.setTextColor(1);
 display.setCursor(40,55);
 display.println("Setup");
 } else

 {
 // display.fillRect(21,10,86,25,1);
 display.setTextColor(1);
 display.setCursor(26,28);
 display.println("Run PCR");

 display.fillRect(21,38,86,25,1);
 display.setTextColor(0);
 display.setCursor(40,55);
 display.println("Setup");
 
  }
  display.setFont();
    display.display();

  }


void draw_run_display()

{
  display.clearDisplay(); 

 display.fillRect(0,0,128,11,1);
  display.setCursor(26,2);
 display.setTextColor(0);
 display.println("PCR Running");
 display.setTextColor(1);

 
  display.setCursor(0,14);
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

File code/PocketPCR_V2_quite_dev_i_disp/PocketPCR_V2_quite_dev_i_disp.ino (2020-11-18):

/*
PocketPCR PCR Thermocycler by GaudiLabs
Pocket size USB powered PCR Thermo Cycler

http://gaudi.ch/PocketPCR/

https://github.com/GaudiLabs/PocketPCR

*/

#include <math.h> 
#include "Adafruit_GFX.h"
#include <Adafruit_SSD1306.h>
#include "Rotary.h"
#include "FlashStorage.h"

#include <Fonts/FreeSans9pt7b.h>

const char VersionString[] = "V1.02 2020";

// These constants won't change. They're used to give names to the pins used:
const int analogInPin = A2;  // Analog input pin that the temperature sensor is attached to
const int fanPin = 4; // Analog output pin that the fan is attached to
const int heaterPin = 8; // Analog output pin that the LED is attached to
const int lidPin = 9; // Analog output pin that the LED is attached to
const int butPin = A4; // Analog output pin that the button is attached to

const int NTC_B = 3435;
const float NTC_TN = 298.15;
const int NTC_RN = 10000;
const float NTC_R0 = 4.7;

const float temperature_tollerance=0.5;
// Rotary encoder is wired with the common to ground and the two
// outputs to pins 6 and 7.
#define ENCODER_1 6
#define ENCODER_2 7
Rotary rotary = Rotary(ENCODER_1, ENCODER_2);

#define SCREEN_WIDTH 128 // OLED display width, in pixels
#define SCREEN_HEIGHT 64 // OLED display height, in pixels


// If using software SPI (the default case):
#define OLED_MOSI   20
#define OLED_CLK   21
#define OLED_DC    0 //11
#define OLED_CS    22 //12
#define OLED_RESET 5

Adafruit_SSD1306 display(SCREEN_WIDTH, SCREEN_HEIGHT,
  OLED_MOSI, OLED_CLK, OLED_DC, OLED_RESET, OLED_CS);
  
#define CASE_Main 1
#define CASE_Settings 2
#define CASE_EditSettings 3
#define CASE_Run 4
#define CASE_Done 5

#define PCR_set 1
#define PCR_transition 2
#define PCR_time 3
#define PCR_end 4


#define PIDp 0.5
#define PIDi 0.0001
#define PIDd 0.15

#define SETTING_Size 6


String SETTING_String[SETTING_Size] = { "Init", "Denature", "Annealing" , "Extension", "Final" };
int SETTING_cycles = 20;

typedef struct {
int value[SETTING_Size*2];
} EEprom;

FlashStorage(my_flash_store, EEprom);
EEprom settings;
  

int sensorValue = 0;        // value read from the sesnor
int outputValue = 0;        // value output to the PWM (heater)
float temperature =0;
float temperature_mean =0;

float sensorResistance =0;
float sensorVoltage =0;

boolean editMode = false;
boolean minuteMode = false;

int counter = 0;        
int counter_save = 0;      

int x=0;
int caseUX = CASE_Main; 
int casePCR = PCR_set;
int MenuItem = 1;
int PCRstate = 0;
int PCRcycle = 1;

int PCRpwm = 0;

float TEMPset;
float TEMPdif;
float TEMPi;
bool PIDIntegration = false;
float TEMPcontrol;
float TEMPdif_a[10];
float TEMPd;
long TEMPclick=0;
long TIMEclick=0;
int TIMEcontrol=0;
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

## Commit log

2019-08-28 First upload PocketPCR is open source
    [GaudiPCR (another copy).kicad_pcb, GaudiPCR (copy).kicad_pcb, GaudiPCR-B.Cu.gbr, GaudiPCR-B.Mask.gbr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]
2019-12-06 New Version with Bottom Heater Improved software
    [BottomHeater (copy).kicad_pcb, BottomHeater-Edge.Cuts.gbr, BottomHeater-F.Cu.gbr, BottomHeater-F.Mask.gbr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]
2020-03-18 Updated PCB, BOM, added Heater Hardware
    [PocketPCR_BOM.ods, RocketPCR-B.Cu.gbr, RocketPCR-B.Mask.gbr, RocketPCR-B.Paste.gbr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]
